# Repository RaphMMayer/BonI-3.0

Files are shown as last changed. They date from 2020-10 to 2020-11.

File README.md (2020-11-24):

# BonI 3.0
Mobile platform for sensory feedback via bone conduction.

The Project gives the PCB, Embedded SW and the API to drive the device via Bluetooth/Wifi.
## Table of Content
* [The PCB](#the-pcb)
  * [Two Layer PCB](#two-layer-pcb)
    * [Components](#components)
    * [Modifications](#modifications)
    * [Connection of the PCB](#connection-of-the-pcb)
    * [Programming and Operation of the PCB](#programming-and-operation-of-the-pcb)
    * [Debugging of the PCB](#debugging-of-the-pcb)
    * [Files](#files)
  * [Four Layer PCB](#four-layer-pcb)
  
* [Schematic](#schematic)
  * [The MCU](#the-mcu)
    * [MCU Pin Connections](#mcu-pin-connections)
  * [Frequency Generator](#frequency-generator)
    * [Frequency Generator Pin Connections](#frequency-generator-pin-connections)
    * [Programming the Frequency Generator](#programming-the-frequency-generator)

## The PCB
### Two Layer PCB:
The two layer PCB is designed as a prototype to our system. The PCB is a two layer board with a poured common ground on the bottom plane for both analogue and digital circuitry. Power traces and signal traces are located mostly on the top plane. With two mounting holes at the side of the PCB it is intended to be contained in the designed box. The PCB is fabricated and assembled by PCBWay.
#### Components:
- A power supply that can regulate 5V input into 3.3V and 5V. The 5V can be sourced from the programmer pins.
- ESP32 as the microcontorller.
- Three AD5932 ICs to generate frequencies.
- Three AD5970 digital potentiometers ICs for controlling the amplitude. 
- Three NCS2211 class AB amplifier ICs.
#### Modifications:
Being the first prototype of our project the PCB is heavily modified.
In order for the PCB to operate normally:
- The unconnected side of resistor C1 needs to be connected to ground.
- One of the unconnected pins of SW1 needs to be connected to ground.
- upper pads of C14 and C15 needs to be connected to provide power to function generators.
- R7, R11, R15, R19, R22 and R25 needs to be desoldered for the correct operation of SPI communications.
- 20K 0402 resistors need to be soldered at R20, R23 and R26 for the amplifier to work.
- The USB footprint J1 is left unused and is not intended to be used.
- Solder 2.56mm connecters to top pin of J1 and the square pin of J1, they are respectively the ground and +5 power supply for the PCB.
#### Connection of the PCB:
The PCB uses 2.56mm connectors for its programming pins and transducer signal output. 2.56mm female jumper headers should be used for proper connection to the system.
The battery port uses standard JST connenctors to fit with most lithium ion batteries.
#### Programming and Operation of the PCB:
The prototype is programmed with Arduino IDE. To program the PCB properly, the following instructions must be followed:
1. Connect TP12 and TP18 to ground. This allows ESP32 to be working in bootloading mode and allows for 3.3V flashing voltage. Failing to do so will result in flash read error.
2. Set the uploading speed to 115200 or above, it will not work with 921600.
3. When uploading the code press and hold SW2, wait until `connecting....`shows up, press and release SW1. This put ESP into flashing mode. Failing to do so will result in `A fatal error occurred: Failed to connect to ESP32: Timed out waiting for packet header`.
4. When it is uploading the code SW2 can now be released.
5. After uploading, `Hard resetting via RTS pin` should be observed,press the SW1 again to reset and boot the program. 
6. Now TP12 and TP18 can be lifted from ground to allow the pins from the MCU to operate as normal I/O pins, but TP18 should be connected to ground when trying to reboot the MCU.
#### Debugging of the PCB:
If encountered any problem, test points near the MCU are available for ruling out errors and faulty circuits.
| Test Point No. |  Net Name | Description |
|----|----|----|
|TP1|CTRL3| The transition from low to high at this pin enable the output of bottom function generator after it being reprogrammed |
|TP2|STANDBY3| Toggle to high to disable the bottom function generator|
|TP3|CTRL2| The transition from low to high at this pin enable the output of middle function generator after it being reprogrammed |
|TP4|CTRL1| The transition from low to high at this pin enable the output of top function generator after it being reprogrammed|
|TP5|STANDBY1|Toggle to high to disable the top function generator|
|TP6|STANDBY2|Toggle to high to disable the middle function generator|
|TP7|SPI1CLK|This pin should provide the clock to all the SPI devices|
|TP8|No connection|Don't Bother|
|TP9|ENABLE1|Toggle to high to turn off the top amplifier(May not work)|
|TP10|ENABLE2|Toggle to high to turn off the middle amplifier(May not work)|
|TP11|SPI1MOSI|This pin should transmit data to all the SPI devices|
|TP12|FSYNC2| This is the slave select pin for the middle function generator, when toggled low it allows the middle function generator to receive data from the MCU|
|TP13|FSYNC3| This is the slave select pin for the bottom function generator, when toggled low it allows the bottom function generator to receive data from the MCU|
|TP14|ENABLE3| Toggle to high to turn off the bottom amplifier(May not work) |
|TP15|SYNC3|This is the slave select pin for the bottom digital potentiometer, when toggled low it allows the bottom digital potentiometer to receive data from the MCU|
|TP16|FSYNC1|This is the slave select pin for the top function generator, when toggled low it allows the top function generator to receive data from the MCU|
|TP17|SYNC1|This is the slave select pin for the top digital potentiometer, when toggled low it allows the top digital potentiometer to receive data from the MCU|
|TP18|SYNC2|This is the slave select pin for the middle digital potentiometer, when toggled low it allows the middle digital potentiometer to receive data from the MCU|
#### Files
All the PCB designs are done in KiCad. The PCB files of the two layer board can be found in the repository. The design is modified so that the aforementioned modifications does not need to be carried out for the two layer board PCB design if the desgin is to be printed in manufactures.
### Four Layer PCB
## Schematic
Both the original and updated version of the schematic can be found in the repository. The schematic is drawn in KiCad. On the first page, there is the frequency generator, amplifier and digital potentiometer. On the second page, there is the MCU and power section. 
### The MCU:
The MCU used in ths project is ESP32-WROOM-32D(4MB)([datasheet](https://www.espressif.com/sites/default/files/documentation/esp32-wroom-32_datasheet_en.pdf)). It mainly serves for communication between the GUI and the frequency generator. Apart from a few pins used for programming, most of the pins are used to communicate with the frequency generators, digital potentiometers and the amplifier.
The MCU communicates with frequency gnerators and digital potentiometers using SPI protocol. The ESP32 has two SPI channels available, and only one of them is utilized. Below are the connections from the MCU.
#### MCU Pin Connections
|Pin No.|Pin Name|Descriptions|
|----|----|----|
|1,15,38|GND|Connected to ground|
|2|DVDD|Power of ESP32, a well regulated 3.3V source is needed|
|3|EN|Reset pin of ESP32, it is connected to a switch, push to reboot the system|
|4|SENSOR_VP|Not used|
|5|SENSOR_VN|Not used|
|6,7,8|IO34 IO35 IO32|Not used|
|9,14,27|IO33 IO12 IO16|SYNC3, SYNC2 and SYNC1, slave select for digital potentiometer|
|10,16,28|IO25 IO13 IO17|ENABLE3, ENABLE2 and ENABLE1, used for turning on and off the amplifier|
|11,23,29|IO26 IO15 IO5|STANDBY3, STANDBY2 and STANDBY1, used for turning on and off the frequency generator|
|12,24,31|IO27 IO2 IO19|FSYNC3, FSYNC2 and FSYNC1, slave select for frequency generator|
|13,26,33|IO14 IO4 IO21|CTRL3, CTRL2 and CTRL1, update the output of the frequency generator|
|17,18,19,20,21,22|SDO SDI SHD SWP SCK SCS| Not used|
|25|IO0| Connected to a switch, hold low and press EN to enter bootloading|
|30|IO18|SPICLK used to synchronize all the SPI devices|
|32|NC|Do not connect|
|34,35|RXD0 TXD0| Serial port used for prgramming, connected to programming pins.|
|36|IO22|Not used.|
|37|IO23|SPIMOSI Used to send SPI data from the MCU|
### Frequency Generator
The frequency generator used in this project is AD5932([datasheet](https://www.analog.com/media/en/technical-documentation/data-sheets/AD5932.pdf)). This is a direct digital synthesis IC that uses SPI communication. It has 24 bits resolution frequency generation derived from the master clock (MCLK) fed in to it. In other words, the frequency it can output can be calculated by MCLK/2^24. We use a MCLK of 32.768kHz for our application. This means we have a frequency range from 0Hz to 32.768kHz with a frequency resolution of 0.00195Hz. It can produce sinusoidal, triangle and square waves at a fixed amplitude of 580 mV peak to peak. The IC also have auto frequency sweeping fucntion, which we are not intended to use in our project. To program the IC properly the MCU must write to AD5932 using SPI communication. 
#### Frequency Generator Pin Connections
|Pin No.|Pin Name|Descriptions|
|----|----|----|
|1|COMP|Decoupled to AVDD|
|2|AVDD|Analog supply (3.3V)|
|3|DVDD|Digital supply (3.3V)|
|4|CAP/2.5V|Decoupled to ground, decoupled to DVDD if DVDD is less than 2.5V|
|5|DGND|Digital Ground|
|6|MCLK|Input master clock from here, connected to SG-3030CM clock generator([datasheet](#https://www5.epsondevice.com/en/products/crystal_oscillator/sg3030cm.html))|
|7|SYNCOUT|Not connected, will output a signal after a frequency sweep(not tested)|
|8|MSBOUT|Not connected, square wave output can be yielded from this port|
|9|Interrupt|Not connected, used to interrupt a frequency sweep|
|10|CTRL|This pin needs to be toggled from low to high to output the frequency written to the frequency generator|
|11|SDATA|The MOSI pin of the device, receive data from SPI master|
|12|SCLK| The SPICLK pin of the device, receive clock from MCU to synchronize the bit transmision|
|13|FSYNC| The slave select pin of the device, pulled low to allow receiving of data|
|14|STANDY| Pull the pin high to disable the frequency generator|
|15|AGND|Analog ground|
|16|VOUT|The output pin for both triangle and sinusoidal wave, switch between the two in software|
#### Programming the Frequency Generator
To program the frequency generator AD5932, a 12 bit data must be written to the 4 bit register with mode 3 SPI communication(CPOL=1 CPHA=0). The following table shows the register used and the data transmitted to each register in the program where the first four bits represent the register written to and the rest are the data bits:
|Function|Data(Binary)|Data(Hexadecimal)|Description|
|--------|---|-----|---|
|Initialize:|	0	0	0	0 1 1 1 0	1 1	0	1	0	0	1	1|0x0ED3|	bit 11 set to one so that both	LSB and MSB are needed to change the outputfrequency. Bit 10 set to 1 to Enable DAC. Bit 9 set to 1	to select sinusoidal wave (0 for triangle wave).	Bit 8 set to 0 for N=no square output(1 for square output from MSBout)	Bit 5 set to 0 to enable automatic frequecny sweep(Don't matter). Bit 3 only matter if bit 2 is set to 1.	Bit 2 set to 0 to not have a pulse at end of sweep(not needed)|	
|No of increment|		0	0	0	1	0	0	0	0	0	0	0	0	0	0	1	0	|0x1002|The bit transmitted should be set to decimal equivalent of 2 for the minimum number of frequency increments(not needed in our case)|
|Period of increment|0	1	1	0	x	x	x	x	x	x	x	x	x	x	x	x|	0x63E8|	Don't care if no frequency sweeping is needed. It is initailized to 1000/MCLK=0.03s|
Frequency Increment LSB|0	0	1	0	0	0	0	0	0	0	0	0	0	0	0	0|0x2000|		Set to 0 if not needed|
Frequency Increment MSB|0	0	1	1	0	0	0	0	0	0	0	0	0	0	0	0	|0x3000|Set to 0 if not needed|																
Start Frequency LSB|1	1	0	0	0	0	0	0	0	0	0	0	0	0	0	0|0xC000|	Set the frequency output. Divide the desired frequency by 0.00195 to yield the data bits.|
Start Frequency MSB	|1	1	1	0	0	0	0	0	0	0	0	0	0	0	0	0|0xD000|Set the frequency output. Divide the desired frequency by 0.00195 to yield the data bits.|

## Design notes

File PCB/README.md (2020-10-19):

# BonI PCB
Included are KiCad files for PCB design, Gerber files as well as bill of materialthat was sent to the manufacturers. The old version of two layer PCB need modifications to be functioning properly. The new version of the two layer PCB is also in the repository.

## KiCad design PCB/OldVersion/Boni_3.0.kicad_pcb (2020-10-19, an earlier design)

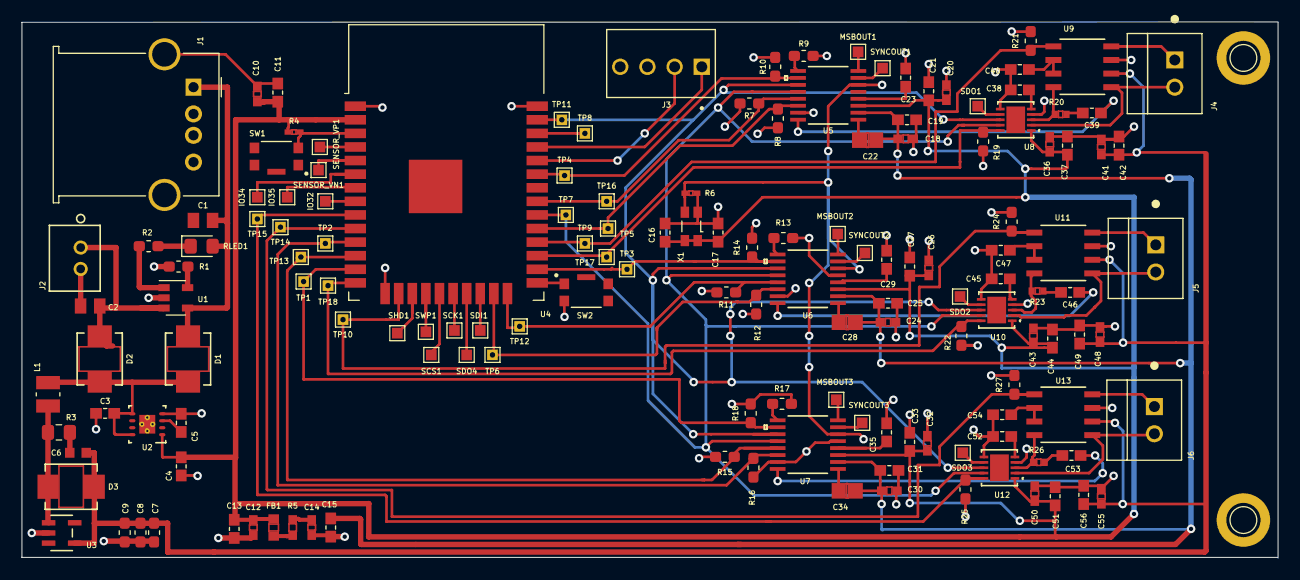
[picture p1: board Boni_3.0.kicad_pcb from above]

Board: 2 copper layers, 117.4 x 50.1 mm, 151 parts (0 on the bottom side), 87 nets.

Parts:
C1, C2: 4.7uF; CAPC2012X95N
C3, C11, C13, C15, C16, C17, C19, C21, C23, C25, C27, C29, C31, C33, C35, C37, C40, C42, C44, C47, C49, C51, C54, C56: 0.1uF; CAPC1608X90
C4, C5, C38, C39, C45, C46, C52, C53: 1uF; CAPC1608X90
C6: 1000pF; CAPC1608X90N
C7, C8, C9: 10uF; C_0603_1608Metric_Pad1.05x0.95mm_HandSolder
C10, C12, C14, C18, C20, C24, C26, C30, C32, C36, C41, C43, C48, C50, C55: 10uF; GRM188R60J106ME84D
C22, C28, C34: 0.01uF; C0805C103J5RAC7210
D1, D2, D3: MBRS340T3G; MBRS130LT3G
Drill1, Drill1#2: Pin_D1.0mm_L10.0mm
FB1: 600Ohm@100MHz; MH1608-601Y
IO32, IO34, IO35: TestPoint; TestPoint_Pad_1.0x1.0mm
J1: USBminiAB; USB_A_Molex_67643_Horizontal
J2: B2B-PH-K-SLFSN
J3: PROG; TE_3-647116-4
J4, J5, J6: Conn_01x02_Male; TE_5-103669-1
L1: 2.2uH; INDC2520X120N
MSBOUT1, MSBOUT2, MSBOUT3: TestPoint; TestPoint_Pad_1.0x1.0mm
R1: 2k; R_0603_1608Metric_Pad1.05x0.95mm_HandSolder
R2: 470; R_0603_1608Metric_Pad1.05x0.95mm_HandSolder
R3: 5; R_0805_2012Metric_Pad1.15x1.40mm_HandSolder
R4, R6: 10k; 10kr
R5: 1.6; 1.6r
R7, R8, R9, R10, R11, R12, R13, R14, R15, R16, R17, R18, R19, R21, R22, R24, R25, R27: 10k; R_0603_1608Metric_Pad1.05x0.95mm_HandSolder
R20, R23, R26: 25k; 20kr
RLED1: SML-D12M1WT86; LED_0805_2012Metric_Pad1.15x1.40mm_HandSolder
SCK1: TestPoint; TestPoint_Pad_1.0x1.0mm
SCS1: TestPoint; TestPoint_Pad_1.0x1.0mm
SDI1: TestPoint; TestPoint_Pad_1.0x1.0mm
SDO1, SDO2, SDO3, SDO4: TestPoint; TestPoint_Pad_1.0x1.0mm
SENSOR_VN1: TestPoint; TestPoint_Pad_1.0x1.0mm
SENSOR_VP1: TestPoint; TestPoint_Pad_1.0x1.0mm
SHD1: TestPoint; TestPoint_Pad_1.0x1.0mm
SW1: SW_Push; SW_KMR421GULCLFS
SW2: SW_DPST_x2; SW_KMR421GULCLFS
SWP1: TestPoint; TestPoint_Pad_1.0x1.0mm
SYNCOUT1, SYNCOUT2, SYNCOUT3: TestPoint; TestPoint_Pad_1.0x1.0mm
TP1: CTRL3; TestPoint_THTPad_1.0x1.0mm_Drill0.5mm
TP2: STANDBY3; TestPoint_THTPad_1.0x1.0mm_Drill0.5mm
TP3: CTRL2; TestPoint_THTPad_1.0x1.0mm_Drill0.5mm
TP4: CTRL1; TestPoint_THTPad_1.0x1.0mm_Drill0.5mm
TP5: STANDBY1; TestPoint_THTPad_1.0x1.0mm_Drill0.5mm
TP6: STANDBY2; TestPoint_THTPad_1.0x1.0mm_Drill0.5mm
TP7: SPI1CLK; TestPoint_THTPad_1.0x1.0mm_Drill0.5mm
TP8: IO22; TestPoint_THTPad_1.0x1.0mm_Drill0.5mm
TP9: ENABLE1; TestPoint_THTPad_1.0x1.0mm_Drill0.5mm
TP10: ENABLE2; TestPoint_THTPad_1.0x1.0mm_Drill0.5mm
TP11: SPIMOSI; TestPoint_THTPad_1.0x1.0mm_Drill0.5mm
TP12: FSYNC2; TestPoint_THTPad_1.0x1.0mm_Drill0.5mm
TP13: FSYNC3; TestPoint_THTPad_1.0x1.0mm_Drill0.5mm
TP14: ENABLE3; TestPoint_THTPad_1.0x1.0mm_Drill0.5mm
TP15: SYNC3; TestPoint_THTPad_1.0x1.0mm_Drill0.5mm
TP16: FSYNC1; TestPoint_THTPad_1.0x1.0mm_Drill0.5mm
TP17: SYNC1; TestPoint_THTPad_1.0x1.0mm_Drill0.5mm
TP18: SYNC2; TestPoint_THTPad_1.0x1.0mm_Drill0.5mm
U1: MCP73831-2-OT; SOT-23-5
U2: TPS73733QDRBRQ1
U3: TPS613222ADBVR
U4: ESP32D; ESP32-WROOM-32
U5, U6, U7: AD5932; AD5932YRUZ
U8, U10, U12: AD5270; AD5270BCPZ-20-RL7
U9, U11, U13: NCS2211
X1: SG-3030CM; Oscillator_SMD_SeikoEpson_SG3030CM

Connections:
+5V: C6.2, C7.1, C8.1, C9.1, C41.1, C42.1, C48.1, C49.1, C55.1, C56.1, D3.1, U3.4, U9.6, U11.6, U13.6
AVDD: C14.1, C15.1, C18.1, C19.1, C22.2, C24.1, C25.1, C28.2, C30.1, C31.1, C34.2, R5.1, U5.2, U6.2, U7.2
CTRL1: R10.1, TP4.1, U4.33, U5.10
CTRL2: R14.1, TP3.1, U4.26, U6.10
CTRL3: R18.1, TP1.1, U4.13, U7.10
DVDD: C4.2, C10.1, C11.1, C12.1, C13.1, C16.1, C17.1, C20.1, C21.1, C26.1, C27.1, C32.1, C33.1, C36.1, C37.1, C43.1, C44.1, C50.1, C51.1, FB1.2, R4.1, U2.1, U4.2, U5.3, U6.3, U7.3, U8.1, U10.1, U12.1, X1.1, X1.4
ENABLE1: R21.1, TP9.1, U4.28, U9.1
ENABLE2: R24.1, TP10.1, U4.16, U11.1
ENABLE3: R27.1, TP14.1, U4.10, U13.1
FSYNC1: R7.1, TP16.1, U4.31, U5.13
FSYNC2: R11.1, TP12.1, U4.24, U6.13
FSYNC3: R15.1, TP13.1, U4.12, U7.13
GND: C1.2, C2.2, C3.2, C4.1, C5.1, C7.2, C8.2, C9.2, C10.2, C11.2, C12.2, C13.2, C14.2, C15.2, C16.2, C17.2, C18.2, C19.2, C20.2, C21.2, C23.2, C24.2, C25.2, C26.2, C27.2, C29.2, C30.2, C31.2, C32.2, C33.2, C35.2, C36.2, C37.2, C38.2, C40.2, C41.2, C42.2, C43.2, C44.2, C45.2, C47.2, C48.2, C49.2, C50.2, C51.2, C52.2, C54.2, C55.2, C56.2, J1.5, J2.2, J3.3, R1.2, R6.2, R7.2, R8.2, R9.2, R10.2, R11.2, R12.2, R13.2, R14.2, R15.2, R16.2, R17.2, R18.2, R19.2, R21.2, R22.2, R24.2, R25.2, R27.2, SW1.1, SW2.2, U1.2, U2.4, U2.9, U3.2, U4.1, U4.15, U4.38, U4.39, U5.5, U5.15, U6.5, U6.15, U7.5, U7.15, U8.4, U8.6, U9.7, U10.4, U10.6, U11.7, U12.4, U12.6, U13.7, X1.2
unnamed: C2.1, D2.2, J2.1, U1.3
unnamed: C3.1, D1.1, D2.1, L1.1, U2.5, U2.8
unnamed: C5.2, U2.3
unnamed: C6.1, R3.1
unnamed: C22.1, U5.1
unnamed: C23.1, U5.4
unnamed: C28.1, U6.1
unnamed: C29.1, U6.4
unnamed: C34.1, U7.1
unnamed: C35.1, U7.4
unnamed: C38.1, U8.5
unnamed: C39.1, R20.2
unnamed: C40.1, U9.2, U9.3
unnamed: C45.1, U10.5
unnamed: C46.1, R23.2
unnamed: C47.1, U11.2, U11.3
unnamed: C52.1, U12.5
unnamed: C53.1, R26.2
unnamed: C54.1, U13.2, U13.3
unnamed: D3.2, L1.2, R3.2, U3.1
unnamed: FB1.1, R5.2
unnamed: IO32.1, U4.8
unnamed: IO34.1, U4.6
unnamed: IO35.1, U4.7
unnamed: J3.1, U4.35
unnamed: J3.2, U4.34
unnamed: J4.1, U9.8
unnamed: J4.2, U8.2, U9.5
unnamed: J5.1, U11.8
unnamed: J5.2, U10.2, U11.5
unnamed: J6.1, U13.8
unnamed: J6.2, U12.2, U13.5
unnamed: MSBOUT1.1, U5.8
unnamed: MSBOUT2.1, U6.8
unnamed: MSBOUT3.1, U7.8
unnamed: R1.1, U1.5
unnamed: R2.1, RLED1.1
unnamed: R2.2, U1.1
unnamed: R4.2, SW1.2, U4.3
unnamed: R6.1, U5.6, U6.6, U7.6, X1.3
unnamed: R9.1, U5.9
unnamed: R13.1, U6.9
unnamed: R17.1, U7.9
unnamed: R20.1, U8.3, U9.4
unnamed: R23.1, U10.3, U11.4
unnamed: R26.1, U12.3, U13.4
unnamed: SCK1.1, U4.20
unnamed: SCS1.1, U4.19
unnamed: SDI1.1, U4.22
unnamed: SDO1.1, U8.7
unnamed: SDO2.1, U10.7
unnamed: SDO3.1, U12.7
unnamed: SDO4.1, U4.21
unnamed: SENSOR_VN1.1, U4.5
unnamed: SENSOR_VP1.1, U4.4
unnamed: SHD1.1, U4.17
unnamed: SW2.1, U4.25
unnamed: SWP1.1, U4.18
unnamed: SYNCOUT1.1, U5.7
unnamed: SYNCOUT2.1, U6.7
unnamed: SYNCOUT3.1, U7.7
unnamed: TP8.1, U4.36
SIN1: C39.2, U5.16
SIN2: C46.2, U6.16
SIN3: C53.2, U7.16
SPI1CLK: TP7.1, U4.30, U5.12, U6.12, U7.12, U8.9, U10.9, U12.9
SPI1MOSI: TP11.1, U4.37, U5.11, U6.11, U7.11, U8.8, U10.8, U12.8
STANDBY1: R8.1, TP5.1, U4.29, U5.14
STANDBY2: R12.1, TP6.1, U4.23, U6.14
STANDBY3: R16.1, TP2.1, U4.11, U7.14
SYNC1: R19.1, TP17.1, U4.27, U8.10
SYNC2: R22.1, TP18.1, U4.14, U10.10
SYNC3: R25.1, TP15.1, U4.9, U12.10
Vusb: C1.1, D1.2, J1.1, RLED1.2, U1.4

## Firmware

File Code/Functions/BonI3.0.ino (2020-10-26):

#include <SPI.h>
#include "BluetoothSerial.h"
#include <WiFi.h>
#include <WiFiClient.h>
#include <WiFiAP.h>



#if !defined(CONFIG_BT_ENABLED) || !defined(CONFIG_BLUEDROID_ENABLED)
#error Bluetooth is not enabled! Please run `make menuconfig` to and enable it
#endif

#define VSPI_MISO   32
#define VSPI_MOSI   23
#define VSPI_SCLK   18

#define FG1_SS     19
#define FG1_CTRL   21
#define FG1_STDB   5

#define DPOT1_SS   16

#define AMP1_EN    17

#define FG2_SS     2
#define FG2_CTRL   4
#define FG2_STDB   15

#define DPOT2_SS   12
#define AMP2_EN    13


#define FG3_SS     27
#define FG3_CTRL   14
#define FG3_STDB   26

#define DPOT3_SS   33

#define AMP3_EN    25

#define FLSB(w) ((uint16_t) ((w) & 0xFFF))
#define FMSB(w) ((uint16_t) ((w) >>12))

//WiFiServer server(80);
BluetoothSerial SerialBT;
//wifi name and password



//const char* ssid = "BonI3.0";
//const char* password = "BonI";
const uint16_t FsLSBReg=0xC000;//frequency start register of AD5932 LSB
const uint16_t FsMSBReg=0xD000;//frequency start register of AD5932 MSB



//uninitalised pointers to SPI objects
SPIClass *vspi = NULL;

void setup() {
  Serial.begin(115200);
  SerialBT.begin("BonI3.0"); //Bluetooth device name
  SerialBT.setTimeout(1);
  Serial.println("The device started, now you can pair it with bluetooth or connect to its WiFi!");
//  Serial.println("Configuring access point...");
//  WiFi.softAP(ssid, password);
//  IPAddress myIP = WiFi.softAPIP();
//  Serial.print("AP IP address: ");
//  Serial.println(myIP);
//  server.begin();
  Serial.println("Server started");
  while(Serial.read()>= 0){}//clear serialport
  //initialise instance of the SPIClass attached to VSPI
  vspi = new SPIClass(VSPI);
  vspi->begin();
  
  pinMode(FG1_SS, OUTPUT); //FG1_ss
  pinMode(FG1_CTRL, OUTPUT); //FG1_ctrl
  pinMode(FG1_STDB, OUTPUT); //FG1_standby
  pinMode(DPOT1_SS, OUTPUT); //DPOT1_ss
  pinMode(AMP1_EN, OUTPUT); //AMP1_enable
  
  pinMode(FG2_SS, OUTPUT); //FG2_ss
  pinMode(FG2_CTRL, OUTPUT); //FG2_ctrl
  pinMode(FG2_STDB, OUTPUT); //FG2_standby
  pinMode(DPOT2_SS, OUTPUT); //DPOT2_ss
  pinMode(AMP2_EN, OUTPUT); //AMP2_enable
  
  pinMode(FG3_SS, OUTPUT); //FG3_ss
  pinMode(FG3_CTRL, OUTPUT); //FG3_ctrl
  pinMode(FG3_STDB, OUTPUT); //FG3_standby
  pinMode(DPOT3_SS, OUTPUT); //DPOT3_ss
  pinMode(AMP3_EN, OUTPUT); //AMP3_enable


  DPOTinit();
  FGinit();
  
}

SPISettings FGsetting(8000000, MSBFIRST, SPI_MODE2);
SPISettings DPOTsetting(1000000, MSBFIRST, SPI_MODE1);


void loop() {
//  WiFiClient client = server.available(); 
//   if (client) {                             // if you get a client,
//    Serial.println("New Client.");           // print a message out the serial port
//    while (client.connected()){
//      if (!client.connected()){
//        Serial.print("connection lost");
//      }
//  else if (client.available()){
//    int Reg1 =client.parseInt();
//    int adata =client.parseInt();
//    int fdata =client.parseInt();
//    int tdata =client.parseInt();
//    
//    Serial.print("The first register is: ");
//    Serial.print(Reg1,HEX);
//    Serial.println();
//
//
//    Serial.print("The Amplitude is: ");
//    Serial.print(adata);
//    Serial.println();
//    
//    Serial.print("The frequency  is: ");
//    Serial.print(fdata);
//    Serial.println();
//    
//    Serial.print("The time is: ");
//    Serial.print(tdata);
//    Serial.println();
//
//    switch(Reg1){
//      case 0:
//        if (adata==1){
//          FG1_STB(0);
//          digitalWrite(AMP1_EN, LOW);//turn on the amplifier
//
//        }
//        else if (adata==0){
//          FG1_STB(1);
//          digitalWrite(AMP1_EN, HIGH);//turn on the amplifier
//        }
//
//        if (fdata==1){
//          FG2_STB(0);
//          digitalWrite(AMP2_EN, LOW);//turn on the amplifier
//
//        }
//        else if(fdata==0) {
//          FG2_STB(1);
//          digitalWrite(AMP2_EN, HIGH);//turn on the amplifier
//        }
//
//        if (tdata==1){
//          FG3_STB(0);
//          digitalWrite(AMP3_EN, LOW);//turn on the amplifier
//
//        }
//        else if(tdata==0){
//          FG3_STB(1);
//          digitalWrite(AMP3_EN, HIGH);//turn on the amplifier
//        }
//      break;
//
//        
//      //check location of device written to: 1 for top,2 for middle and 3 for bottom
//      case 1:
//        DPOT1_WR(adata);
//        FG1_STB(0);
//        FG1_WR(fdata);
//        digitalWrite(AMP1_EN, LOW);//turn on the amplifier
//        FG1_ON();
//        if (tdata>0){
//        delay(tdata);
//        FG1_STB(1);
//        digitalWrite(AMP1_EN, HIGH);//turn off the amplifier
//        }
//        break;
//      case 2:
//        DPOT2_WR(adata);
//        FG2_STB(0);
//        FG2_WR(fdata);
//        digitalWrite(AMP2_EN, LOW);//turn on the amplifier
//        FG2_ON();
//        if (tdata>0){
//        delay(tdata);
//        FG2_STB(1);
//        digitalWrite(AMP2_EN, HIGH);//turn off the amplifier
//        }
//        break;
//      case 3:
//        DPOT3_WR(adata);
//        FG3_STB(0);
//        FG3_WR(fdata);
//        digitalWrite(AMP3_EN, LOW);//turn on the amplifier
//        FG3_ON();
//        if (tdata>0){
//        delay(tdata);
//        FG3_STB(1);
//        digitalWrite(AMP3_EN, HIGH);//turn off the amplifier
//        }
//        break; 
//  }
//  }
//   }
//    
//   }
//  else 
if (SerialBT.available()) {
    int Reg1 =SerialBT.parseInt();
    int adata =SerialBT.parseInt();
    int fdata =SerialBT.parseInt();
    int tdata =SerialBT.parseInt();
    
    Serial.print("The first register is: ");
    Serial.print(Reg1,HEX);
    Serial.println();


    Serial.print("The Amplitude is: ");
    Serial.print(adata);
    Serial.println();
    
    Serial.print("The frequency  is: ");
    Serial.print(fdata);
    Serial.println();
    
    Serial.print("The time is: ");
    Serial.print(tdata);
    Serial.println();

    switch(Reg1){
      case 0:
        if (adata==1){
          FG1_STB(0);
          digitalWrite(AMP1_EN, LOW);//turn on the amplifier

        }
        else if (adata==0){
          FG1_STB(1);
          digitalWrite(AMP1_EN, HIGH);//turn on the amplifier
        }

        if (fdata==1){
          FG2_STB(0);
          digitalWrite(AMP2_EN, LOW);//turn on the amplifier

        }
        else if(fdata==0) {
          FG2_STB(1);
          digitalWrite(AMP2_EN, HIGH);//turn on the amplifier
        }

        if (tdata==1){
          FG3_STB(0);
          digitalWrite(AMP3_EN, LOW);//turn on the amplifier

        }
        else if(tdata==0){
          FG3_STB(1);
          digitalWrite(AMP3_EN, HIGH);//turn on the amplifier
        }
      break;

        
      //check location of device written to: 1 for top,2 for middle and 3 for bottom
      case 1:
        DPOT1_WR(adata);
        FG1_STB(0);
        FG1_WR(fdata);
        digitalWrite(AMP1_EN, LOW);//turn on the amplifier
        FG1_ON();
        if (tdata>0){
        delay(tdata);
        FG1_STB(1);
        digitalWrite(AMP1_EN, HIGH);//turn off the amplifier
        }
        break;
      case 2:
        DPOT2_WR(adata);
        FG2_STB(0);
        FG2_WR(fdata);
        digitalWrite(AMP2_EN, LOW);//turn on the amplifier
        FG2_ON();
        if (tdata>0){
        delay(tdata);
        FG2_STB(1);
        digitalWrite(AMP2_EN, HIGH);//turn off the amplifier
        }
        break;
      case 3:
        DPOT3_WR(adata);
        FG3_STB(0);
        FG3_WR(fdata);
        digitalWrite(AMP3_EN, LOW);//turn on the amplifier
        FG3_ON();
        if (tdata>0){
        delay(tdata);
        FG3_STB(1);
        digitalWrite(AMP3_EN, HIGH);//turn off the amplifier
        }
        break; 
    }
  }
  }
void FGinit(){
  vspi->beginTransaction(FGsetting);
  
  digitalWrite(FG1_SS, LOW);
  delay(1);
  vspi->transfer16(0xED3); //Initialize setting
  digitalWrite(FG1_SS, HIGH);
  delay(1);
  
  digitalWrite(FG1_SS, LOW);
  delay(1);
  vspi->transfer16(0x63E8);//Period of increment=1000
  digitalWrite(FG1_SS, HIGH);
  delay(1);
  
  digitalWrite(FG1_SS, LOW);
  delay(1);
  vspi->transfer16(0x2000);//LSB increment frequency=0
  digitalWrite(FG1_SS, HIGH);
  delay(1);
  
  digitalWrite(FG1_SS, LOW);
  delay(1);
  vspi->transfer16(0x3000);//MSB increment frequency=0
  digitalWrite(FG1_SS, HIGH);
  delay(1);
  
  digitalWrite(FG1_SS, LOW);
  delay(1);
  vspi->transfer16(0x1002);//Increment step=2(minimum)
  digitalWrite(FG1_SS, HIGH);
  delay(1);
  
  digitalWrite(FG1_SS, LOW);
  delay(1);
  vspi->transfer16(0xC000);// LSB initialize frequency(0)
  digitalWrite(FG1_SS, HIGH);
  delay(1);
  
  digitalWrite(FG1_SS, LOW);
  delay(1);
  vspi->transfer16(0xD000);// MSB initialize frequency(0)
  digitalWrite(FG1_SS, HIGH);
  delay(1);

  //FG2
  digitalWrite(FG2_SS, LOW);
  delay(1);
  vspi->transfer16(0xED3); //Initialize setting
  digitalWrite(FG2_SS, HIGH);
  delay(1);
  
  digitalWrite(FG2_SS, LOW);
  delay(1);
  vspi->transfer16(0x63E8);//Period of increment=1000
  digitalWrite(FG2_SS, HIGH);
  delay(1);
  
  digitalWrite(FG2_SS, LOW);
  delay(1);
  vspi->transfer16(0x2000);//LSB increment frequency=0
  digitalWrite(FG2_SS, HIGH);
  delay(1);
  
  digitalWrite(FG2_SS, LOW);
  delay(1);
  vspi->transfer16(0x3000);//MSB increment frequency=0
  digitalWrite(FG2_SS, HIGH);
  delay(1);
  
  digitalWrite(FG2_SS, LOW);
  delay(1);
  vspi->transfer16(0x1002);//Increment step=2(minimum)
  digitalWrite(FG2_SS, HIGH);
  delay(1);
  
  digitalWrite(FG2_SS, LOW);
  delay(1);
  vspi->transfer16(0xC000);// LSB initialize frequency(0)
  digitalWrite(FG2_SS, HIGH);
  delay(1);
  
  digitalWrite(FG2_SS, LOW);
  delay(1);
  vspi->transfer16(0xD000);// MSB initialize frequency(0)
  digitalWrite(FG2_SS, HIGH);
  delay(1);

//FG3
  digitalWrite(FG3_SS, LOW);
  delay(1);
  vspi->transfer16(0xED3); //Initialize setting
  digitalWrite(FG3_SS, HIGH);
  delay(1);
  
  digitalWrite(FG3_SS, LOW);
  delay(1);
  vspi->transfer16(0x63E8);//Period of increment=1000
  digitalWrite(FG3_SS, HIGH);
  delay(1);
  
  digitalWrite(FG3_SS, LOW);
  delay(1);
  vspi->transfer16(0x2000);//LSB increment frequency=0
  digitalWrite(FG3_SS, HIGH);
  delay(1);
  
  digitalWrite(FG3_SS, LOW);
  delay(1);
  vspi->transfer16(0x3000);//MSB increment frequency=0
  digitalWrite(FG3_SS, HIGH);
  delay(1);
  
  digitalWrite(FG3_SS, LOW);
  delay(1);
  vspi->transfer16(0x1002);//Increment step=2(minimum)
  digitalWrite(FG3_SS, HIGH);
  delay(1);
  
  digitalWrite(FG3_SS, LOW);
  delay(1);
  vspi->transfer16(0xC000);// LSB initialize frequency(0)
  digitalWrite(FG3_SS, HIGH);
  delay(1);
  
  digitalWrite(FG3_SS, LOW);
  delay(1);
  vspi->transfer16(0xD000);// MSB initialize frequency(0)
  digitalWrite(FG3_SS, HIGH);
  delay(1);
  
  vspi->endTransaction();
}

void DPOTinit(){
  vspi->beginTransaction(DPOTsetting);
  digitalWrite(DPOT1_SS, LOW);
  delay(10);
  //  send in the address and value via SPI:
  vspi->transfer16(0x1C03);
  delay(10);
  // take the SS pin high to de-select the chip:
  digitalWrite(DPOT1_SS, HIGH);

  digitalWrite(DPOT2_SS, LOW);
  delay(10);
  //  send in the address and value via SPI:
  vspi->transfer16(0x1C03);
  delay(10);
  // take the SS pin high to de-select the chip:
  digitalWrite(DPOT2_SS, HIGH);

  digitalWrite(DPOT3_SS, LOW);
  delay(10);
  //  send in the address and value via SPI:
  vspi->transfer16(0x1C03);
  delay(10);
  // take the SS pin high to de-select the chip:
  digitalWrite(DPOT3_SS, HIGH);
  vspi->endTransaction();
}
void DPOT1_WR(int ampl) {
  // take the SS pin low to select the chip:
  vspi->beginTransaction(DPOTsetting);

  digitalWrite(DPOT1_SS, LOW);
  delay(10);
  //  send in the address and value via SPI:
  vspi->transfer16(0x0400+ampl/2);
  delay(10);
  // take the SS pin high to de-select the chip:
  digitalWrite(DPOT1_SS, HIGH);
  vspi->endTransaction();
}
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

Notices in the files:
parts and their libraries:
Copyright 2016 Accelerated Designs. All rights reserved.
